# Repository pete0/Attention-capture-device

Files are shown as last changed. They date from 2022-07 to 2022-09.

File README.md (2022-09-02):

# An ‘Attention Capture Device’ for capturing facial images of pumas or other wildlife in camera trapping studies

### Peter Alexander
### <a href="https://www.beringiasouth.org/">Craighead Beringia South</a> - Kelly, WY

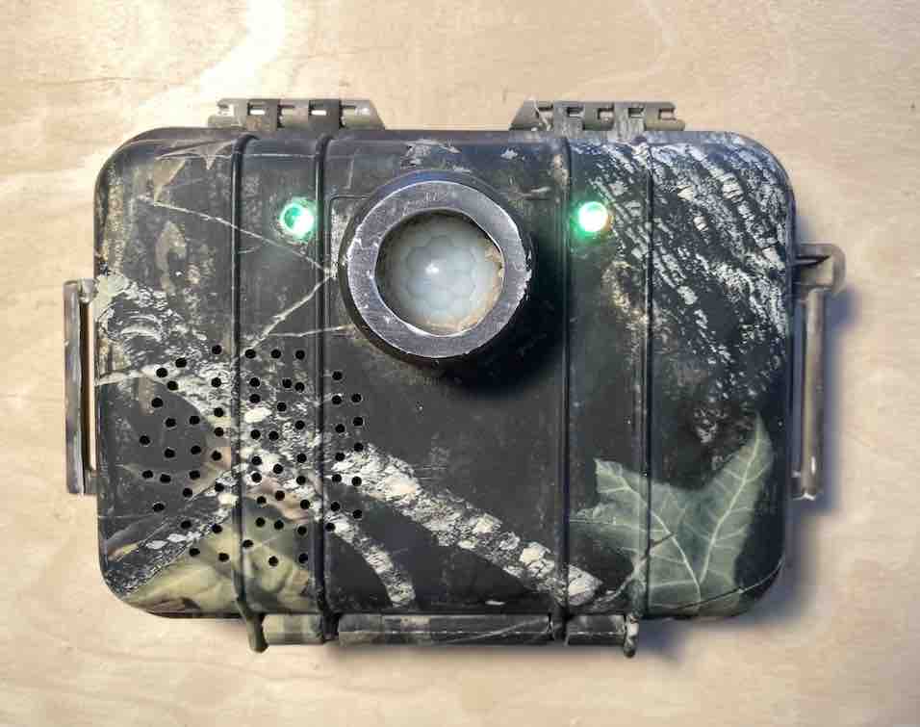
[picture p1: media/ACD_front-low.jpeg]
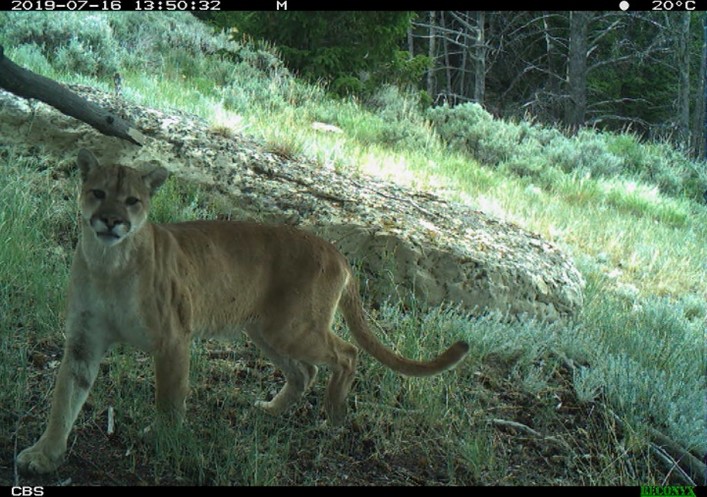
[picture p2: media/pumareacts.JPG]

<br clear="both"/>

The Attention Capture Device (ACD) was designed to help capture facial images of pumas in camera trapping studies, in order to improve researcher ability to identify individual pumas. See <a href="https://onlinelibrary.wiley.com/doi/10.1002/ece3.8536">our article published in Ecology & Evolution</a> for more details on the research; here, I describe the technical design of the ACD.

I designed this device to be very low-cost, low-power, and as simple as possible to deploy alongside a conventional camera trap. The ACD operates entirely independently of a camera trap. It is mounted adjacent to a camera trap (of any type), with the sensor aimed in the same direction as the camera’s; when a passing animal triggers the camera, it will also trigger the ACD.

When triggered, the ACD’s two LED lights will illuminate (mimicking eye-shine), and it will play a sound. I programmed the units to play the sound of a cougar kitten ‘chirp’, although any sound could be programmed into the chip (with some work). The target animal, with any luck, will turn its attention to the ACD to investigate, thereby presenting its face to the camera as well:

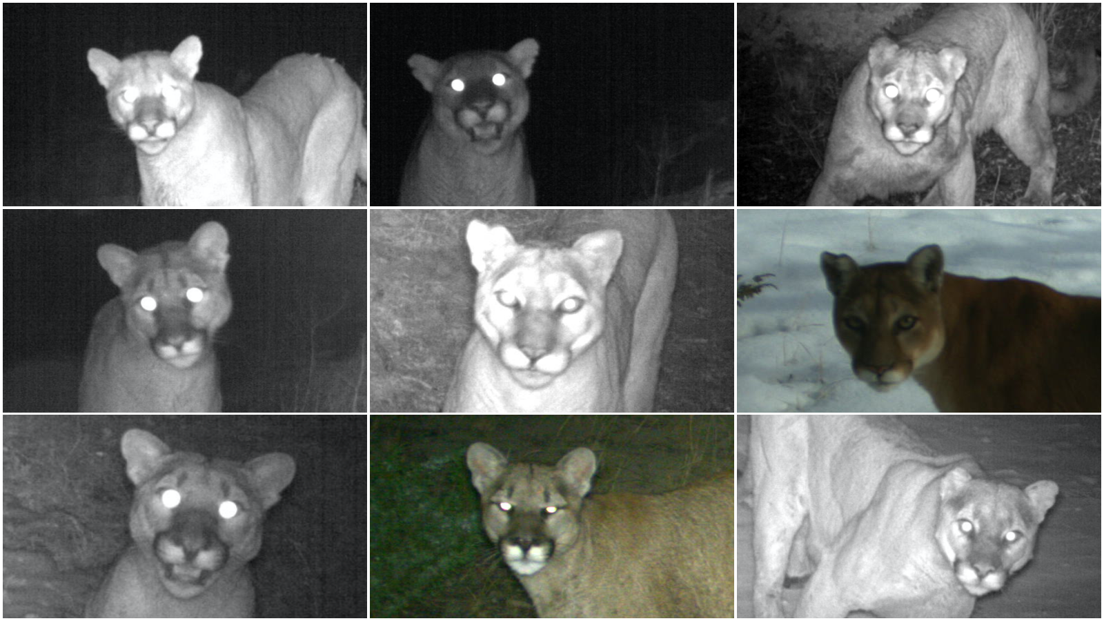
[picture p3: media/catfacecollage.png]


## Basic design
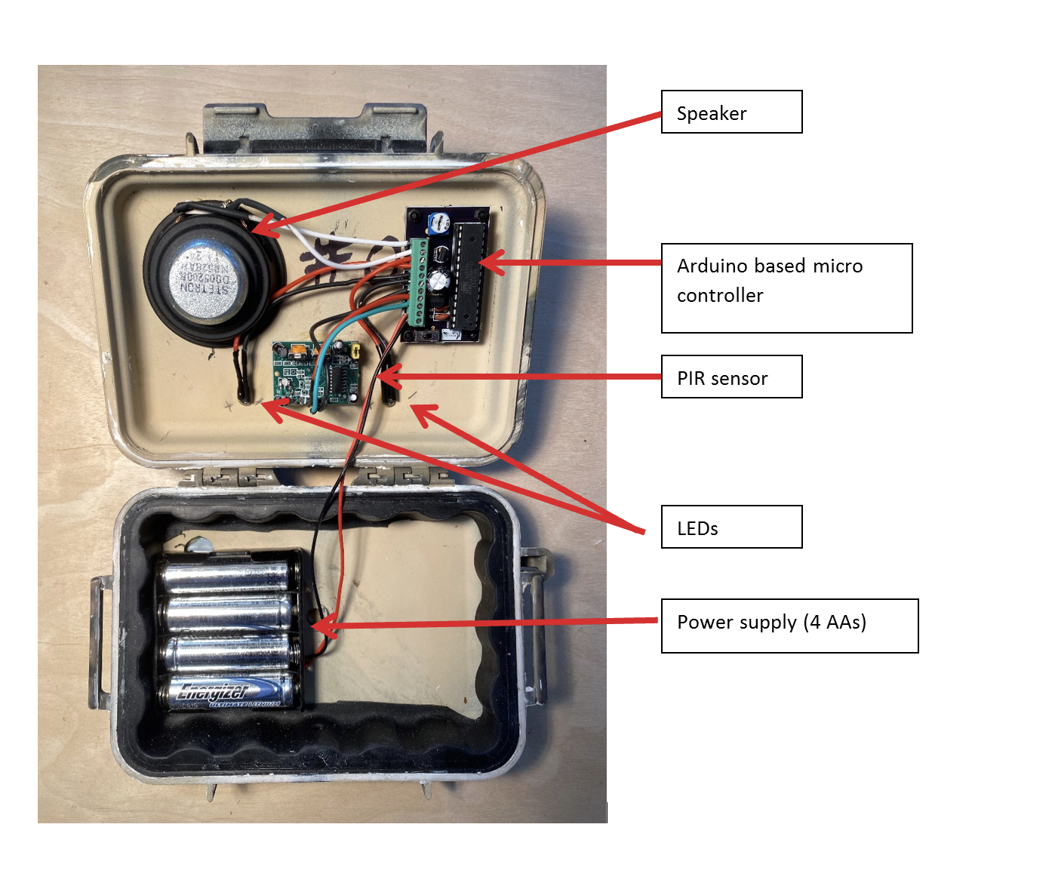
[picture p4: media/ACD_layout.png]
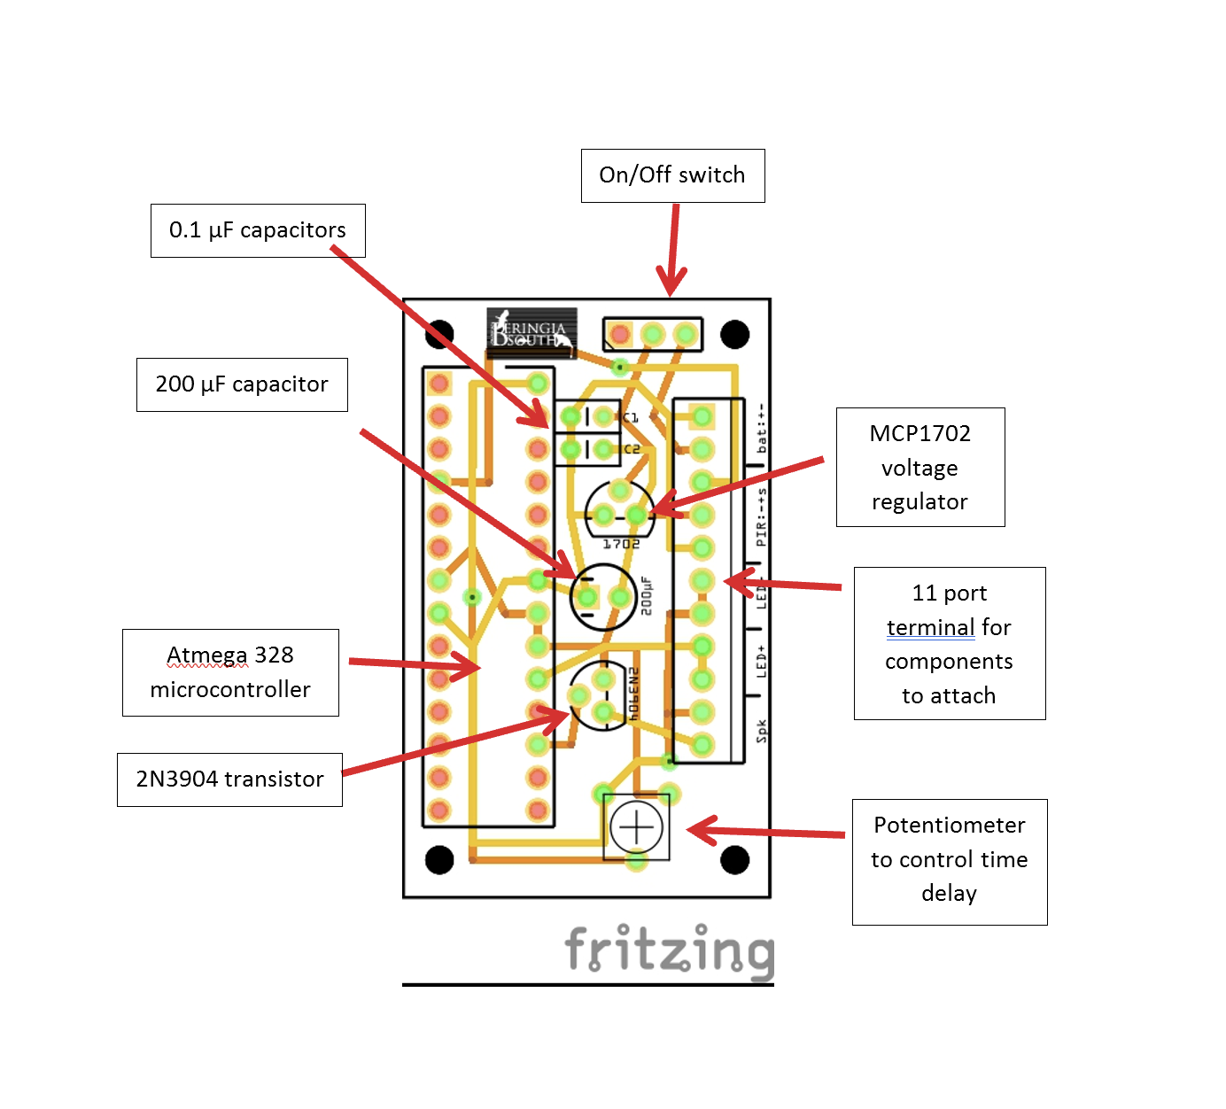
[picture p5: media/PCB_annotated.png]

<br clear="both"/>

The electrical components are all reletively inexpensive, at roughly $15 per ACD; The waterproof case (I used a Pelican 1020 micro-case) is the most expensive part at about $15-$25 per box; sometimes cheap used ones can be found (e.g., on eBay). Note that additional hardware is required for uploading code to the Atmega (computer, Arduino board, cables, breadboard, etc).

## Arduino platform
The device uses the <a href="https://www.arduino.cc/">Arduino**®** framework</a> to operate. Arduino is an open-source hardware/software system commonly used by hobbyists, students or other ‘prototypers’ for lightweight automated or robotic applications. There is a large online community for Arduino, and almost any question can be answered by searching the Arduino forums or google.

To reduce the power as much as possible, I used a 'barebones' setup, with an Atmega328 as the controller. An Arduino Uno board was used to upload the programming to the Atmega : https://docs.arduino.cc/built-in-examples/arduino-isp/ArduinoToBreadboard

## Schematic
The design is based around the Atmega328p, with a voltage regulator, an on switch, a transistor to amplify the sound, a few capacitors, and the delay timer to change how quickly the sound is activated after being triggered. I had circuit boards printed at <a href="https://oshpark.com/">OSH Park</a>, drawn to include an 11-pin screw terminal to make attaching the components (PIR, LED lights, battery pack, speaker) easy.

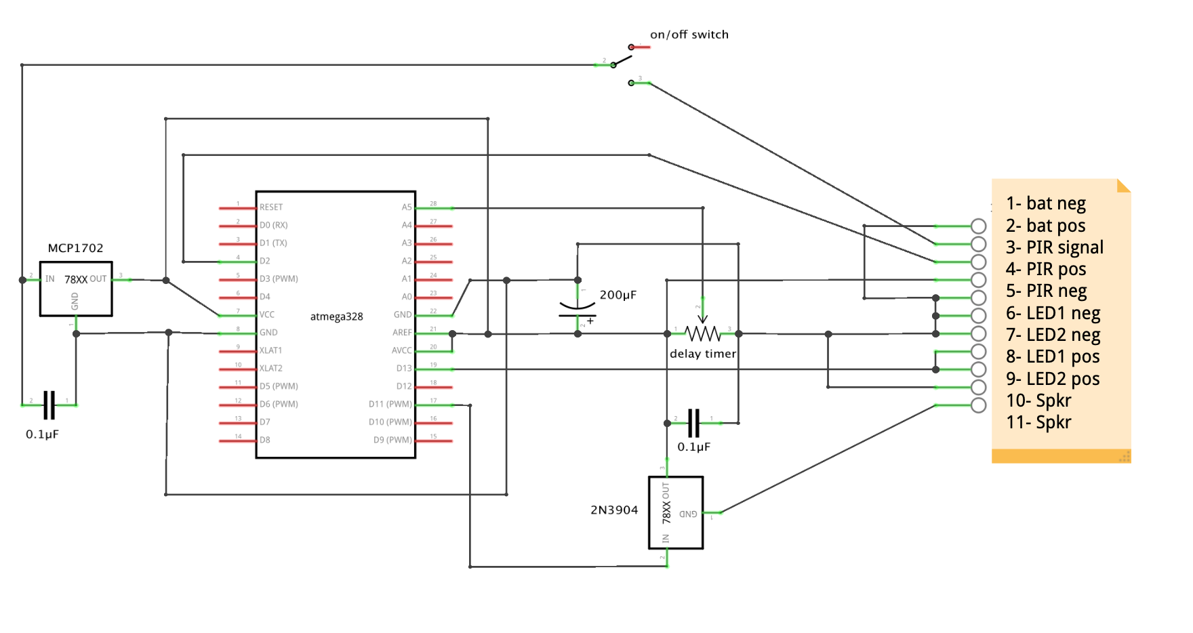
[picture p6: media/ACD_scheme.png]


## Programming
All programming was written with the Arduino IDE: https://www.arduino.cc/en/software

The <a href="code/controller.ino">main ACD code</a> controls the manner in which the unit starts up, goes into and out of sleep mode, activates the lights and speaker, and calls the libraries for sleep and audio functions.

More on the sleep libraries found here: https://www.nongnu.org/avr-libc/user-manual/group__avr__sleep.html and https://www.gammon.com.au/power

## Sound
I use an 8 Ohm speaker. For simplicity and power-savings, the sound is converted from wav and coded directly into the controller code:  see https://playground.arduino.cc/Code/PCMAudio/

In my code, I included several short audio clips of puma 'chirps'; when triggered they are played in random order.

## PIR
The PIR is a standard HC-SR501, but modified to bypass its voltage regulator and run off of the 3.3V output of the microcontroller:
https://forum.mysensors.org/topic/1088/battery-powered-pir

I also attached a small tube on front of the PIR window to act as a 'blinder' so motion on the periphery does not trigger the ACD too early.

## Power
The ACD runs on 4 AA batteries. I used Energizer "ultimate lithium" batteries, and could expect the ACD to run for several months.

## Settings
The only "settings" that could be changed when deploying the ACD are on the PIR <a href="https://create.arduino.cc/projecthub/electropeak/pir-motion-sensor-how-to-use-pirs-w-arduino-raspberry-pi-18d7fa">(see here)</a>, and the built-in delay timer. Details:
 <ul>
  <li>PIR 3 pin 'jumper': leave on H</li>
  <li>PIR sensitivity: turned clockwise for higher sensitivity </li>
  <li>PIR timeout: turned counter-clockwise for a short timeout</li>
  <li>Delay timer : turn clockwise for a longer delay between motion and sound (the lights are always activated immediately)</li>
</ul> 

## Camera trapping setup
The device is mounted immediately next to a camera trap; I used 1/4" bolts to attach both camera and ACD to a small piece of wood, which was then strapped to a tree:
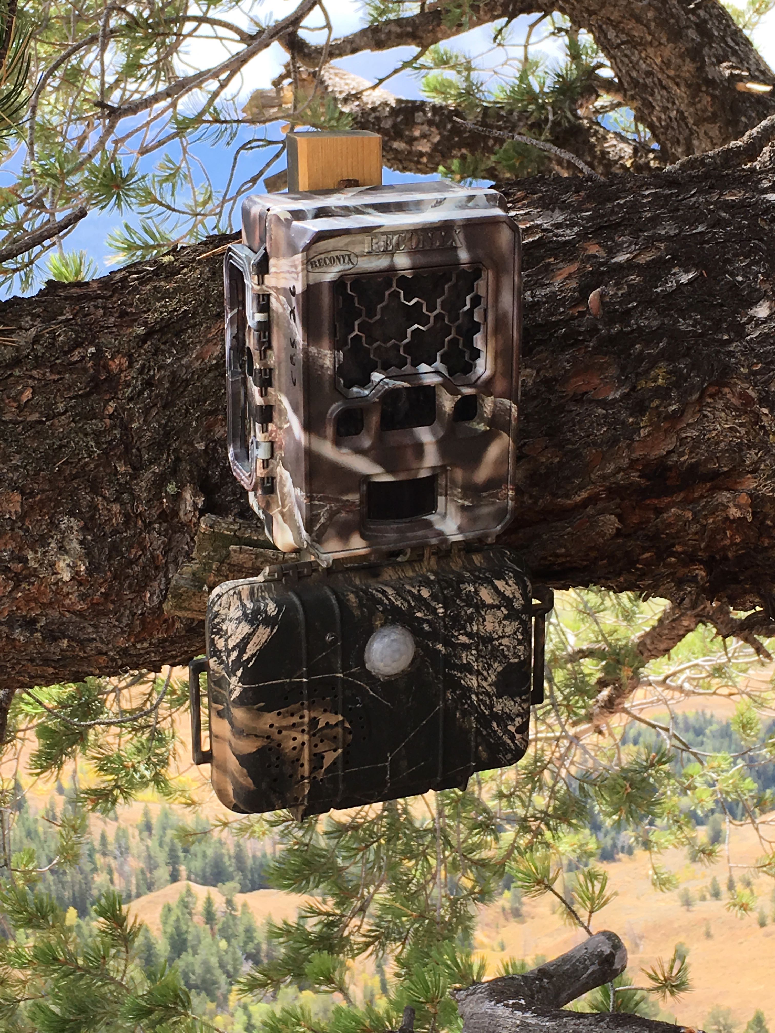
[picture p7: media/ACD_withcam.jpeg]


The device is simply switched on at deployment; a series of beeps and clicks indicate a countdown to activation. If altering the PIR or the delay timer, the unit should be reset by switching off and back on.

I had the best results when I used a scent lure, placed on the ground +/- 3m from the camera in the center of the field of view. By setting the delay timer, this allows an animal to fully enter the camera's field of view to first investigate the scent, before the sound is triggered.

## Final thoughts
 <ul>
  <li>I designed this in 2017-2018; undoubtedly some of the software and hardware has become obsolete, or better options have become available</li>
  <li> The sound is fairly poor quality; not sure what effect this may have had on animal reactions (curiosity vs fear) </li>
 <li> Animals were sometimes a little too far back, or too far to the side to capture a clear image of their face - improvements to the camera type/placement/lens could help </li>
 <li> I typically used Reconyx Hyperfire or Ultrafire cameras. Videos seemed to have a higher chance of capturing a face image (i.e., a quick glance was potentially missed if a camera was set to take still images).
 <li> Motion was not detected 100%; a higher quality PIR and/or improving my circuit design could improve this</li>
 <li> Obviosuly, this technique eliminates the 'covertness' of a typical camera trap. Prey species (elk and deer for my study) had mixed reactions, and were sometimes quite 'spooked'; bears sometimes pulled it down; potential human reactions should also be considered when choosing where to place these traps </li>
</ul>

####
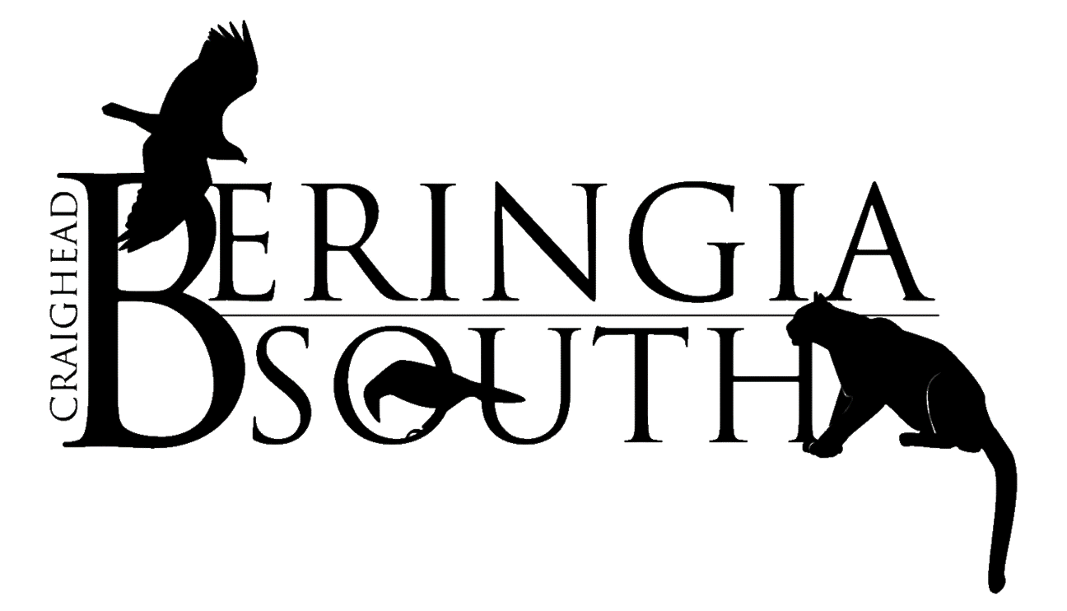
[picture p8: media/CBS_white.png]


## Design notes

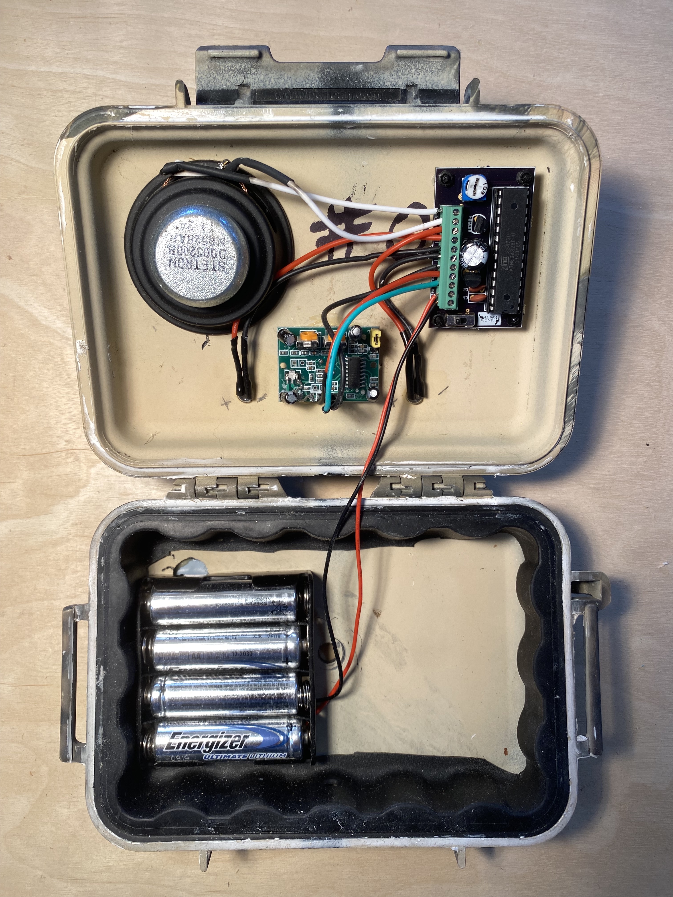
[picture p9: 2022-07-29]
media/ACD_inside.jpg

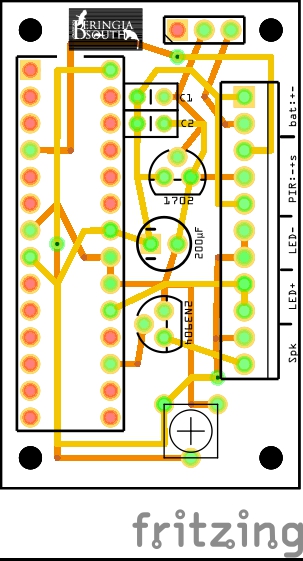
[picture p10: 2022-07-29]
media/PCB.jpg

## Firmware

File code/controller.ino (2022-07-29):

#include <PCM.h>
#include <avr/sleep.h>
#include <avr/interrupt.h>


      

long unsigned int lowIn;         

long unsigned int pause = 3000;

boolean lockLow = true;
boolean takeLowTime;  

const uint8_t PotPin   = A5;   // Potentiometer
int speakPin = 11;
int pirPin = 2;    //the digital pin connected to the PIR sensor's output
int ledPin = 13;
int counterstart = 0;
int counter = counterstart;
boolean trig;
int tmDelay;

const unsigned char chirp1[] PROGMEM = {
129, 128, 128, 129, 128, 127, 127, 128, 129, 127, 127, 128, 127, 128, 129, 127, 127, 129, 128, 126, 128, 129, 127, 127, 129, 128, 128, 128, 128, 128, 128, 128, 128, 127, 128, 128, 127, 127, 127, 128, 128, 128, 128, 127, 128, 128, 127, 128, 128, 128, 127, 127, 129, 128, 128, 129, 128, 128, 128, 127, 129, 129, 126, 128, 129, 127, 127, 129, 127, 127, 128, 129, 129, 126, 128, 129, 128, 127, 129, 129, 127, 128, 129, 127, 126, 129, 130, 126, 128, 131, 127, 126, 130, 128, 125, 128, 129, 127, 127, 128, 128, 128, 128, 127, 128, 130, 126, 126, 130, 127, 124, 130, 132, 123, 124, 135, 129, 119, 131, 137, 119, 121, 141, 130, 111, 132, 143, 118, 115, 142, 139, 111, 120, 149, 130, 104, 133, 154, 114, 103, 152, 148, 95, 120, 166, 123, 91, 148, 157, 95, 111, 165, 129, 92, 139, 158, 107, 102, 156, 152, 93, 109, 171, 131, 77, 146, 174, 86, 99, 187, 127, 65, 159, 175, 76, 104, 184, 129, 77, 147, 173, 90, 99, 178, 131, 80, 147, 162, 100, 104, 156, 147, 95, 117, 169, 121, 84, 156, 161, 83, 116, 183, 113, 73, 168, 168, 66, 115, 201, 103, 61, 190, 163, 46, 137, 203, 81, 82, 198, 139, 59, 153, 180, 78, 103, 186, 120, 74, 162, 159, 77, 128, 173, 105, 106, 156, 132, 108, 130, 141, 124, 120, 134, 130, 124, 126, 127, 133, 125, 116, 137, 139, 108, 122, 159, 121, 95, 157, 150, 77, 128, 184, 93, 85, 192, 139, 54, 158, 185, 65, 109, 205, 100, 66, 195, 149, 48, 157, 190, 61, 108, 206, 95, 69, 200, 141, 51, 164, 179, 56, 119, 202, 86, 86, 202, 122, 56, 174, 169, 59, 127, 197, 87, 88, 194, 119, 73, 182, 149, 61, 156, 173, 66, 130, 189, 84, 102, 191, 107, 74, 187, 142, 53, 168, 182, 51, 124, 206, 77, 79, 212, 122, 51, 195, 159, 36, 159, 196, 48, 110, 215, 82, 71, 213, 122, 54, 197, 154, 38, 163, 190, 45, 121, 213, 75, 84, 209, 109, 54, 188, 149, 46, 166, 184, 52, 131, 198, 72, 103, 200, 100, 86, 191, 123, 80, 174, 136, 81, 157, 145, 86, 147, 149, 87, 143, 158, 90, 134, 158, 91, 125, 164, 101, 112, 166, 120, 100, 149, 141, 105, 122, 150, 121, 103, 151, 140, 92, 138, 161, 94, 110, 176, 111, 81, 177, 142, 67, 159, 168, 62, 131, 195, 73, 94, 215, 106, 54, 204, 150, 30, 169, 191, 37, 131, 221, 59, 80, 227, 107, 40, 206, 161, 23, 164, 205, 39, 123, 230, 71, 75, 225, 114, 37, 196, 168, 34, 152, 205, 52, 100, 215, 88, 66, 210, 134, 47, 175, 173, 59, 136, 191, 85, 97, 182, 117, 80, 164, 152, 83, 135, 171, 99, 106, 169, 122, 91, 153, 146, 92, 127, 162, 111, 101, 160, 139, 88, 143, 162, 91, 116, 169, 115, 94, 158, 150, 86, 125, 176, 103, 89, 179, 136, 69, 159, 165, 67, 121, 189, 94, 80, 192, 135, 53, 166, 177, 56, 133, 199, 70, 96, 205, 110, 65, 190, 155, 51, 152, 189, 64, 107, 204, 97, 72, 198, 142, 52, 160, 187, 61, 106, 207, 104, 64, 184, 153, 52, 145, 195, 71, 95, 203, 118, 57, 178, 172, 56, 126, 193, 89, 81, 190, 134, 60, 163, 171, 68, 124, 191, 96, 89, 185, 135, 76, 153, 162, 79, 123, 177, 92, 95, 177, 126, 80, 161, 158, 78, 127, 178, 101, 89, 178, 135, 65, 155, 172, 71, 115, 196, 104, 71, 185, 153, 53, 143, 197, 73, 90, 206, 118, 54, 180, 171, 53, 130, 204, 84, 81, 204, 133, 52, 167, 180, 58, 119, 197, 90, 82, 192, 130, 59, 170, 169, 60, 135, 196, 81, 89, 200, 117, 59, 183, 162, 49, 144, 201, 62, 95, 220, 108, 45, 198, 173, 29, 139, 219, 61, 75, 225, 121, 29, 190, 188, 31, 126, 229, 75, 57, 218, 147, 32, 166, 201, 53, 101, 211, 104, 66, 190, 149, 55, 148, 181, 76, 110, 186, 110, 88, 168, 134, 88, 152, 147, 89, 142, 159, 87, 125, 178, 98, 93, 184, 127, 66, 169, 166, 61, 134, 201, 75, 79, 214, 125, 37, 181, 194, 34, 114, 231, 82, 53, 216, 156, 24, 161, 207, 45, 99, 228, 104, 42, 202, 169, 35, 140, 208, 74, 82, 202, 120, 63, 172, 159, 68, 138, 180, 82, 110, 182, 110, 90, 172, 135, 80, 154, 149, 82, 141, 172, 82, 110, 189, 103, 76, 186, 149, 55, 153, 188, 62, 104, 209, 102, 63, 200, 153, 37, 153, 202, 54, 94, 222, 109, 47, 191, 169, 43, 143, 204, 67, 90, 209, 114, 57, 188, 161, 49, 144, 191, 68, 97, 201, 108, 72, 189, 144, 54, 157, 184, 60, 117, 208, 89, 72, 205, 142, 45, 172, 188, 43, 114, 215, 83, 62, 215, 144, 34, 173, 199, 43, 106, 226, 89, 52, 210, 153, 32, 161, 209, 52, 100, 223, 103, 52, 195, 159, 42, 147, 195, 67, 97, 200, 111, 70, 182, 149, 64, 149, 174, 77, 120, 185, 97, 91, 186, 123, 69, 175, 162, 58, 137, 200, 74, 89, 206, 122, 51, 179, 175, 42, 129, 209, 79, 73, 210, 138, 40, 171, 189, 59, 109, 208, 99, 69, 190, 142, 62, 152, 177, 67, 114, 189, 99, 89, 180, 137, 72, 163, 157, 69, 137, 187, 83, 89, 204, 120, 51, 178, 186, 50, 110, 219, 95, 57, 194, 165, 45, 136, 206, 78, 78, 195, 144, 58, 147, 181, 84, 103, 175, 129, 87, 148, 150, 99, 124, 148, 120, 114, 141, 131, 118, 132, 131, 128, 129, 125, 126, 138, 121, 111, 144, 136, 105, 130, 156, 110, 104, 161, 138, 92, 134, 165, 106, 104, 162, 133, 94, 138, 155, 100, 115, 160, 120, 100, 151, 146, 95, 131, 162, 112, 103, 157, 140, 94, 133, 155, 106, 109, 157, 131, 98, 137, 151, 109, 118, 150, 124, 114, 142, 134, 111, 142, 141, 103, 127, 159, 115, 95, 161, 148, 88, 124, 173, 113, 91, 166, 145, 85, 129, 172, 100, 95, 174, 139, 77, 135, 178, 95, 96, 173, 138, 83, 141, 167, 93, 114, 171, 121, 87, 159, 157, 80, 119, 178, 115, 79, 161, 158, 85, 119, 173, 114, 89, 163, 147, 85, 128, 179, 101, 86, 173, 155, 75, 116, 189, 112, 76, 154, 169, 88, 103, 174, 127, 93, 136, 159, 107, 118, 154, 121, 111, 140, 147, 105, 130, 148, 117, 110, 138, 141, 105, 128, 139, 125, 118, 132, 133, 122, 137, 126, 122, 134, 142, 117, 117, 149, 130, 103, 126, 156, 117, 99, 151, 153, 94, 112, 175, 127, 77, 154, 180, 79, 92, 200, 143, 41, 147, 212, 74, 62, 208, 166, 30, 134, 214, 83, 65, 201, 152, 40, 154, 195, 66, 89, 216, 123, 38, 181, 190, 49, 96, 222, 111, 49, 183, 171, 56, 118, 199, 88, 83, 193, 136, 59, 160, 186, 55, 105, 214, 116, 43, 177, 193, 47, 99, 220, 127, 43, 166, 193, 67, 93, 202, 135, 53, 154, 188, 80, 93, 201, 142, 51, 141, 195, 85, 71, 194, 158, 53, 126, 201, 98, 70, 187, 155, 54, 134, 205, 82, 70, 206, 154, 35, 139, 223, 75, 59, 208, 155, 28, 141, 220, 70, 70, 218, 141, 18, 163, 232, 47, 55, 242, 161, 0, 143, 255, 69, 26, 223, 193, 12, 109, 244, 99, 30, 199, 195, 32, 106, 233, 102, 29, 195, 197, 28, 99, 239, 104, 22, 196, 206, 25, 94, 250, 110, 11, 196, 221, 23, 78, 254, 128, 6, 179, 231, 39, 65, 239, 144, 16, 156, 224, 62, 62, 218, 159, 35, 136, 213, 89, 60, 183, 166, 62, 120, 198, 108, 66, 172, 177, 66, 99, 205, 133, 45, 153, 218, 79, 46, 200, 191, 40, 93, 231, 132, 23, 155, 218, 67, 58, 214, 168, 30, 126, 230, 94, 35, 196, 203, 40, 78, 226, 146, 24, 134, 219, 98, 52, 176, 184, 71, 93, 188, 140, 68, 137, 181, 102, 88, 174, 158, 72, 115, 192, 124, 63, 153, 187, 80, 80, 192, 160, 56, 121, 203, 110, 60, 175, 188, 63, 91, 205, 139, 48, 145, 206, 88, 62, 186, 179, 58, 99, 205, 137, 52, 137, 202, 99, 59, 172, 188, 69, 84, 206, 157, 39, 117, 225, 113, 32, 166, 214, 66, 56, 209, 174, 35, 107, 228, 120, 35, 165, 208, 67, 62, 213, 166, 25, 113, 241, 117, 20, 174, 228, 61, 48, 223, 179, 24, 114, 239, 106, 23, 188, 216, 45, 63, 230, 159, 17, 123, 231, 102, 32, 173, 200, 73, 76, 195, 162, 62, 117, 197, 129, 59, 143, 191, 105, 66, 160, 181, 80, 83, 181, 162, 64, 106, 191, 137, 64, 134, 190, 106, 71, 164, 187, 80, 79, 191, 175, 54, 88, 214, 149, 31, 127, 237, 111, 22, 175, 231, 61, 47, 224, 186, 19, 105, 247, 125, 14, 162, 229, 70, 50, 205, 184, 45, 101, 218, 139, 46, 141, 214, 103, 53, 167, 201, 82, 65, 184, 186, 71, 83, 198, 157, 58, 115, 199, 127, 57, 145, 197, 101, 63, 169, 186, 85, 81, 179, 168, 71, 102, 192, 145, 55, 126, 203, 121, 54, 147, 202, 98, 66, 170, 183, 75, 92, 190, 158, 66, 105, 192, 139, 67, 121, 186, 123, 74, 135, 181, 120, 75, 147, 172, 108, 88, 155, 162, 95, 99, 159, 155, 91, 99, 161, 155, 88, 88, 163, 173, 94, 84, 177, 180, 83, 85, 188, 177, 67, 93, 201, 166, 61, 101, 204, 158, 60, 109, 201, 157, 64, 113, 196, 149, 71, 125, 196, 127, 76, 142, 183, 106, 80, 164, 170, 90, 94, 170, 158, 92, 103, 169, 152, 94, 112, 170, 152, 79, 113, 186, 153, 72, 109, 199, 144, 66, 121, 192, 134, 72, 131, 181, 129, 84, 128, 162, 126, 101, 124, 146, 134, 110, 124, 147, 136, 118, 118, 135, 143, 129, 112, 121, 145, 150, 109, 98, 156, 162, 96, 91, 166, 167, 89, 90, 173, 168, 78, 101, 172, 150, 78, 100, 189, 146, 70, 106, 184, 156, 60, 108, 189, 142, 67, 115, 198, 133, 59, 132, 203, 121, 58, 138, 194, 121, 61, 139, 194, 120, 67, 130, 189, 137, 66, 111, 189, 147, 78, 105, 173, 162, 92, 96, 163, 167, 110, 86, 142, 183, 119, 63, 125, 204, 128, 40, 119, 221, 150, 23, 111, 234, 162, 29, 84, 233, 178, 37, 70, 220, 197, 40, 62, 223, 199, 36, 54, 220, 215, 32, 46, 212, 212, 57, 33, 189, 215, 81, 41, 165, 212, 106, 56, 143, 199, 122, 74, 135, 181, 137, 83, 113, 173, 154, 91, 83, 159, 185, 104, 66, 144, 204, 127, 58, 122, 208, 148, 57, 93, 197, 182, 63, 74, 184, 204, 67, 48, 181, 210, 84, 22, 177, 229, 91, 21, 161, 239, 104, 15, 144, 246, 109, 29, 130, 226, 133, 43, 117, 197, 149, 73, 107, 152, 163, 112, 90, 125, 159, 144, 91, 96, 158, 178, 92, 79, 159, 192, 104, 53, 146, 205, 114, 42, 137, 196, 138, 64, 116, 186, 145, 96, 108, 142, 145, 135, 108, 101, 131, 173, 133, 70, 111, 198, 155, 49, 105, 205, 152, 44, 105, 209, 154, 43, 109, 199, 152, 78, 90, 169, 162, 113, 84, 126, 165, 160, 85, 83, 173, 178, 107, 48, 159, 201, 122, 43, 129, 217, 138, 60, 92, 212, 149, 80, 82, 175, 166, 94, 94, 132, 176, 107, 115, 100, 158, 144, 119, 103, 115, 177, 130, 110, 78, 183, 146, 104, 86, 137, 184, 103, 110, 101, 171, 132, 141, 81, 120, 167, 141, 120, 62, 176, 149, 135, 66, 142, 160, 127, 111, 90, 175, 116, 147, 92, 145, 128, 145, 125, 100, 151, 104, 174, 82, 141, 116, 156, 138, 92, 137, 120, 187, 73, 124, 116, 175, 130, 76, 140, 142, 177, 65, 126, 138, 179, 110, 71, 153, 164, 157, 58, 123, 161, 176, 93, 78, 158, 154, 145, 82, 115, 158, 138, 117, 105, 126, 159, 127, 112, 109, 143, 154, 126, 106, 111, 166, 132, 126, 89, 139, 163, 115, 110, 99, 170, 133, 111, 102, 148, 158, 103, 118, 117, 169, 115, 107, 136, 133, 148, 94, 137, 147, 126, 115, 109, 160, 121, 123, 114, 142, 145, 94, 143, 119, 154, 106, 113, 157, 121, 133, 99, 163, 135, 116, 107, 135, 163, 106, 117, 115, 172, 116, 103, 120, 151, 162, 82, 118, 124, 160, 132, 107, 126, 128, 138, 118, 137, 116, 133, 125, 130, 135, 107, 140, 141, 130, 110, 116, 142, 149, 118, 102, 133, 136, 143, 115, 119, 136, 127, 138, 130, 127, 114, 130, 149, 133, 110, 97, 145, 156, 123, 102, 113, 155, 143, 112, 116, 130, 137, 121, 129, 138, 118, 116, 129, 157, 130, 92, 117, 158, 160, 98, 84, 145, 180, 130, 82, 109, 162, 164, 108, 98, 128, 148, 139, 115, 123, 123, 119, 136, 143, 128, 102, 116, 154, 155, 113, 93, 123, 158, 155, 100, 101, 127, 149, 156, 115, 111, 111, 141, 164, 131, 100, 100, 136, 168, 143, 91, 96, 136, 171, 144, 99, 95, 129, 170, 153, 107, 81, 125, 168, 161, 108, 77, 122, 166, 167, 112, 87, 116, 148, 159, 130, 97, 101, 133, 163, 150, 98, 88, 129, 170, 156, 97, 84, 138, 165, 145, 110, 96, 134, 145, 140, 129, 108, 116, 137, 149, 139, 108, 101, 147, 156, 132, 105, 109, 152, 142, 122, 118, 127, 135, 123, 127, 143, 130, 109, 118, 141, 156, 118, 99, 128, 144, 148, 118, 112, 128, 130, 135, 136, 124, 112, 114, 134, 159, 127, 100, 113, 138, 155, 126, 108, 120, 132, 135, 133, 127, 125, 119, 121, 143, 138, 117, 113, 127, 144, 138, 118, 120, 127, 135, 131, 124, 131, 123, 122, 127, 136, 132, 124, 122, 127, 134, 131, 128, 119, 131, 134, 129, 127, 120, 129, 140, 133, 118, 116, 130, 147, 126, 117, 118, 123, 143, 132, 126, 118, 117, 132, 141, 140, 117, 108, 130, 149, 131, 113, 118, 134, 139, 121, 120, 134, 137, 123, 115, 137, 144, 120, 113, 132, 146, 132, 113, 119, 139, 137, 121, 120, 134, 136, 116, 123, 142, 138, 115, 110, 133, 145, 133, 116, 118, 135, 133, 126, 127, 128, 128, 118, 130, 139, 128, 123, 121, 131, 127, 130, 132,
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
